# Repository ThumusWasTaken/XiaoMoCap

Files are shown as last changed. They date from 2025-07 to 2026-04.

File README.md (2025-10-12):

Guide to build and code you TOL, tiny open logger IMU sensor:

1- Arduino code folder:
TinyOpenLogger_Code

2- PCB CAD files folder:
KiCad_files

3- 3D print link: 
https://cad.onshape.com/documents/7f3e29c87ee979af035eb522/w/dbec0ba7e6f450b7338eaabc/e/624f816bbdc67f06185ccd3e?renderMode=0&uiState=68eb8f6068579bafa34129be

4- JLC PCB order folder:
JLCorder_withLED

5- Web user interface code folder:
HTMLWebUI

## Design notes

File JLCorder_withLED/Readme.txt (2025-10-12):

These Files are to be used directly on https://jlcpcb.com/

1- Upload the esp_bmi_withLED_GBR.zip in Add gerber file
2- Select wanted PCB options - this is a 2-layer PCB
3- If you wan to add th component assembly, select PCB Assembly and tick Assemble top side
4- Click next twice
5- In section: Bill of Materials, add BOM file: esp_bmi270_mlx90393_withLED and CPL file: esp_bmi270_mlx90393-pos_numbered_withLED.

Note: The Xiao ESP32-C3 is added to the CPL but is not part of the PCB, a window "Project has unselected parts" will show when pressing Next, select "Do not place".
In the window component placement, make sure the purple dots of each component is aligned with the dot/arrow/star on the silkscreen.

Note2: I the case of a component out of stock, look for an alternative on https://jlcpcb.com/parts, make sure the foot print is the same and modify the CPL file with the corresponding JLCPCB Part #.

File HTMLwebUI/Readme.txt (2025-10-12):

WebUI Instructions:

Activate WiFi: Press the Xiao sensor button.
(LED flashes quickly, then turns OFF)
Connect: Join TOL-xxx WiFi network.
Configure:
Use the UI to configure rate and duration and click “Send Config”, or
Long press the sensor button (< 4 sec) to use default config.
(LED ON)
Start Recording: Press the sensor button.
(LED slow flash — WiFi off, data recording)
Stop Recording:
Wait for configured duration, or
Long press (< 4 sec) to stop early.
(LED quick flash — data ready)
Upload Data:
Press button to re-enable WiFi.
Reconnect to TOL-xxx WiFi and click “Connect” on UI.
(LED ON — data is sending)
Download:
Click “Download CSV” to save data early, it will automatically download when complete.
(LED OFF — finished)

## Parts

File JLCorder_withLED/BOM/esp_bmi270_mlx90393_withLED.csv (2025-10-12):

Comment | Designator | Footprint | LCSC Part #
100 nF Unpolarized capacitor | C201,C202,C301,C302,C401 | C_0402_1005Metric | C1525
LED Light emitting diode | D101 | LED_Kingbright_APA1606_1.6x0.6mm_Horizontal | C3034753
220 Resistor | R101 | R_0402_1005Metric | C25091
4.7k Resistor | R201,R202,R203,R401,R402,R403 | R_0402_1005Metric | C25900
XIAO ESP32 C3 | U1 | DIP-14_600_ELL | C19189385
BMI270 | U2 | LGA-14 2.5x3mm | C2836813
MLX90393ELW-ABA-011-RE | U3 | QFN-16-1EP_3x3mm_P0.5mm_EP1.675x1.675mm | C2654971
W25N01GVZEIG | U4 | WSON-8_8X6_WIN | C907680

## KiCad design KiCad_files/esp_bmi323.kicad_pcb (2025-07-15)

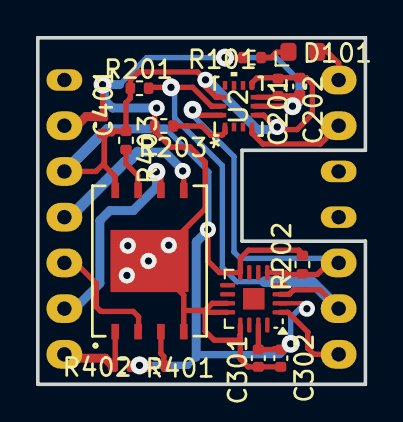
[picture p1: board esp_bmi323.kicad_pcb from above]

Board: 2 copper layers, 18.2 x 19.2 mm, 17 parts (1 on the bottom side), 14 nets.

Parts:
C201, C202, C301, C302, C401: 100 nF; C_0402_1005Metric
D101: LED; LED_Kingbright_APA1606_1.6x0.6mm_Horizontal
R101: 220; R_0402_1005Metric
R201, R202, R203, R401, R402, R403: 4.7k; R_0402_1005Metric
U1: XIAO ESP32 C3; DIP-14_600_ELL
U2: BMI323; BMI323_BOS
U3: MLX90393; QFN-16-1EP_3x3mm_P0.5mm_EP1.675x1.675mm
U4: W25N01GVZEIG; WSON-8_8X6_WIN

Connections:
+3.3V: C201.1, C202.1, C301.2, C302.2, C401.2, R201.1, R202.1, R401.1, R402.1, R403.1, U1.12 (3V3), U2.5 (VDDIO), U2.8 (VDD), U2.12 (CSB), U3.2 (MS/~CS), U3.8 (VDDIO), U3.15 (VDD), U4.8 (VCC)
GND: C201.2, C202.2, C301.1, C302.1, C401.1, R101.2, R203.2, U1.13 (GND), U2.6 (GNDIO), U2.7 (GND), U3.11 (A1), U3.12 (A0), U3.13 (GND), U4.4 (GND), U4.9 (GND)
GPIO7_MLX90393: U1.7 (GPIO7), U3.1 (INT)
GPIO44_W25N: R402.2, U1.8 (RX), U4.1 (/CS)
MISO_W25N: U1.10 (MISO), U4.2 (DO(IO1))
MOSI_W25N: U1.11 (MOSI), U4.5 (DI(IO0))
unnamed: D101.2 (A), U1.1 (GPIO2)
unnamed: D101.1 (K), R101.1
unnamed: R203.1, U2.1 (SDO)
unnamed: R403.2, U4.7 (/HOLD(IO3))
unnamed: R401.2, U4.3 (/WP(IO2))
SCK_W25N: U1.9 (SCK), U4.6 (CLK)
SCL_BMI323: R201.2, U1.6 (SCL), U2.13 (SCX), U3.3 (SCL/SCLK)
SDA_BMI323: R202.2, U1.5 (SDA), U2.14 (SDX), U3.5 (SDA/MOSI)

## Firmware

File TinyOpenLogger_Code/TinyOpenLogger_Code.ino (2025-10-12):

#include <Wire.h>
#include <time.h>
#include "W25N01GV.h"
#include "BadBlockManager.h"
#include "Logger.h"

#include <Arduino_BMI270_BMM150.h>
#include <Adafruit_MLX90393.h>

#include <WiFi.h>
#include <WebServer.h>

// Flash
#define FLASH_CS D7
W25N01GV flash(FLASH_CS);
BadBlockManager bbm(flash);
Logger logger(flash, bbm);

uint32_t data_num = 0;
// Sensors
bool acc_active = true;
bool gyr_active = true;
bool mag_active = true;
uint32_t duration_ms = 60000;       // Default: 60 seconds
uint16_t sample_rate_hz = 10;       // Default: 10 Hz
bool configReceived = false;
Adafruit_MLX90393 mag = Adafruit_MLX90393();

// Switch and LED settings
#define LED_PIN 2        // D0 on XIAO ESP32-C3 (GPIO2)
#define BUTTON_PIN 9     // BOOT button is on GPIO9
volatile bool buttonInterruptTriggered = false;
unsigned long lastInterruptTime = 0;
const unsigned long debounceDelay = 200;  // ms debounce
bool interruptsAllowed = false;
volatile bool longPressDetected = false;
unsigned long buttonPressStart = 0;
bool buttonHeld = false;

// WiFi credentials for Access Point
const char* ssid = "TOL-001";
const char* password = "12345678";

// Configurable IP settings
IPAddress local_IP(192, 168, 1, 100);  // Change this IP as needed
IPAddress gateway(192, 168, 1, 1);
IPAddress subnet(255, 255, 255, 0);

// Create WebServer object on port 80
WebServer server(80);

String dat = "";

void shutdownWiFi() {
  WiFi.disconnect(true);
  WiFi.mode(WIFI_OFF);
  Serial.println("Wi-Fi turned off.");
}

void startWiFi() {
  WiFi.mode(WIFI_AP);                      // Set Wi-Fi mode to AP
  WiFi.softAPConfig(local_IP, gateway, subnet);  // Configure IP
  WiFi.softAP(ssid, password);             // Start AP
  Serial.println("Wi-Fi Access Point restarted");
}


void handleData() {
  server.sendHeader("Access-Control-Allow-Origin", "*");
  server.setContentLength(CONTENT_LENGTH_UNKNOWN);
  server.send(200, "text/csv", "");
  server.sendContent("timestamp,ax,ay,az,gx,gy,gz,mx,my,mz,counter\n");

  uint8_t readBuf[PAGE_SIZE];
  uint32_t lastPage = logger.getCurrentPage();

  for (uint32_t page = 0; page < lastPage; page++) {
    if (!bbm.isBlockGood(page / 64)) continue;
    if (!flash.readPage(page, readBuf, sizeof(readBuf))) continue;

    PageHeader *hdr = (PageHeader*)readBuf;
    if (hdr->magic != PAGE_MAGIC) continue;

    for (uint16_t i = 0; i < RECORDS_PER_PAGE; i++) {
      SensorRecord *rec = (SensorRecord*)(readBuf + HEADER_SIZE + i * RECORD_SIZE);
      if (rec->timestamp == 0xFFFFFFFF) break;

      char line[128];
      int len = snprintf(line, sizeof(line),
        "%lu,%d,%d,%d,%d,%d,%d,%d,%d,%d,%lu\n",
        rec->timestamp,
        rec->ax, rec->ay, rec->az,
        rec->gx, rec->gy, rec->gz,
        rec->mx, rec->my, rec->mz,
        rec->counter);
      server.sendContent_P(line, len);
    }
    delay(1);
  }

  server.sendContent("");
}

void handleLoggingConfig() {
  if (server.hasArg("duration") && server.hasArg("rate")) {
    for (int i = 0; i < server.args(); i++) {
      Serial.printf(" - %s = %s\n", server.argName(i).c_str(), server.arg(i).c_str());
    }

    duration_ms = server.arg("duration").toInt() * 1000UL;
    sample_rate_hz = server.arg("rate").toInt();
    
    acc_active = (server.arg("accelerometer") == "true");
    gyr_active = (server.arg("gyroscope") == "true");
    mag_active = (server.arg("magnetometer") == "true");

    if (duration_ms == 0) duration_ms = 60000;
    if (sample_rate_hz == 0 || sample_rate_hz > 100) sample_rate_hz = 10;

    configReceived = true;

    Serial.printf("✔ Config received: %lu ms, %u Hz\n", duration_ms, sample_rate_hz);
    Serial.printf("✔ Config received: accel: %, gyro: %, magne: %", acc_active, gyr_active, mag_active);
    server.send(200, "text/plain", "✔ Logging config received.");
  } else {
    server.send(400, "text/plain", "❌ Missing 'duration' or 'rate' parameter.");
  }
}

// Function to properly disable SPI to free up GPIO9
void disableSPIForButton() {
  // End SPI communication
  SPI.end();
  // Set CS high to deselect flash
  digitalWrite(FLASH_CS, HIGH);
  // Configure GPIO9 as input with pullup for button
  pinMode(BUTTON_PIN, INPUT_PULLUP);
  // Small delay to let pin settle
  delay(10);
  
  Serial.println("SPI disabled, GPIO9 configured for button");
}

// Function to re-enable SPI for flash access
void enableSPIForFlash() {
  // Reconfigure SPI
  SPI.begin();
  // Reinitialize flash
  flash.setSPIFrequency(1000000);
  // Set CS as output and select flash
  pinMode(FLASH_CS, OUTPUT);
  digitalWrite(FLASH_CS, LOW);
  // Small delay to let SPI settle
  delay(10);
  
  Serial.println("SPI re-enabled for flash access");
}

void IRAM_ATTR handleButtonPress() {
  if (!interruptsAllowed) return;  // Ignore until setup is done

  unsigned long currentTime = millis();
  if ((currentTime - lastInterruptTime) > debounceDelay) {
    buttonInterruptTriggered = true;
    lastInterruptTime = currentTime;
  }
}

void setup() {
  //Serial.begin(115200);
  Serial.begin(921600);
  delay(1000);
  Serial.println("Starting multi-sensor NAND logger...");

  // I2C setup (Xiao ESP32-C3: SDA = 8, SCL = 9)
  Wire.begin();
  Wire.setClock(400000);
  delay(100);

  // --- Flash setup ---
  flash.setSPIFrequency(1000000);
  if (!flash.begin()) {
    Serial.println("Flash init failed!"); while (1);
  }
  flash.clearBlockProtection();
  flash.setECCEnabled(true);
  bbm.scan();
  if (!logger.begin()) {
    Serial.println("Logger init failed!"); while (1);
  }

  Serial.println("Erasing flash... this may take a few seconds.");
  logger.eraseAll();
  Serial.println("Flash erase complete.");

  // Set initial time
  struct tm timeinfo;
  timeinfo.tm_year = 2025 - 1900;
  timeinfo.tm_mon = 5;
  timeinfo.tm_mday = 30;
  timeinfo.tm_hour = 14;
  timeinfo.tm_min = 0;
  timeinfo.tm_sec = 0;
  time_t t_of_day = mktime(&timeinfo);
  struct timeval now = { .tv_sec = t_of_day };
  settimeofday(&now, NULL);

  // --- BMI270 init ---
  if (!IMU.begin()) {
    Serial.println("BMI270 not detected!");
    while (1);
  }
  Serial.println("BMI270 connected!");
  Serial.print("Accelerometer rate = ");
  Serial.println(IMU.accelerationSampleRate());
  Serial.print("Gyroscope rate = ");
  Serial.println(IMU.gyroscopeSampleRate());

  // --- MLX90393 init ---
  if (!mag.begin_I2C()) {
    Serial.println("MLX90393 not detected!");
    while (1);
  }
  Serial.println("MLX90393 connected.");
  mag.setGain(MLX90393_GAIN_1X);
  mag.setResolution(MLX90393_X, MLX90393_RES_16);
  mag.setResolution(MLX90393_Y, MLX90393_RES_16);
  mag.setResolution(MLX90393_Z, MLX90393_RES_16);
  mag.setOversampling(MLX90393_OSR_0);
  mag.setFilter(MLX90393_FILTER_2);

  delay(10);

  // Configure Access Point with custom IP
  WiFi.softAPConfig(local_IP, gateway, subnet);
  WiFi.softAP(ssid, password);
  
  IPAddress IP = WiFi.softAPIP();
  
  Serial.println("=== ESP32 Data Server Started ===");
  Serial.println("WiFi SSID: " + String(ssid));
  Serial.println("WiFi Password: " + String(password));
  Serial.println("Server IP: " + IP.toString());
  Serial.println("Endpoints:");
  Serial.println("  http://" + IP.toString() + "/data (CSV)");
  Serial.println("  http://" + IP.toString() + "/json (JSON)");
  Serial.println("===================================");

  // Set up web server routes
  //server.on("/", handleRoot);
  server.on("/data", handleData);
  server.on("/send", handleLoggingConfig);

  // Start server
  server.begin();
  Serial.println("HTTP server started");

  
  //Internal LED setup
  pinMode(LED_PIN, OUTPUT);
  digitalWrite(LED_PIN, LOW);  // Ensure it's off initially
  //Boot button setup
  pinMode(BUTTON_PIN, INPUT_PULLUP);
  // Wait for button to be released and settle
  while (digitalRead(BUTTON_PIN) == LOW) {
    Serial.println("Waiting for button release...");
    delay(50);
  }
  // Small delay to ensure pin settles
  delay(100);
  // Attach interrupt but don't allow it to trigger yet
  attachInterrupt(digitalPinToInterrupt(BUTTON_PIN), handleButtonPress, FALLING);
  // Set debounce timer
  lastInterruptTime = millis();
}
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

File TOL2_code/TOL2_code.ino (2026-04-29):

/**
 * BMI270 IMU Logger with SdFat  |  XIAO ESP32S3
 * ─────────────────────────────────────────────
 * Uses SdFat instead of the built-in SD library.
 * SdFat writes in 512-byte aligned blocks which avoids
 * the partial-write corruption seen with the SD library
 * on long recordings.
 *
 * Libraries (Arduino Library Manager):
 *   - Arduino_BMI270_BMM150
 *   - SdFat  by Bill Greiman
 *
 * Wiring:
 *   BMI270  SDA → D4,  SCL → D5  (I2C)
 *   SD      CS  → D2,  SCK → D7, MOSI → D9, MISO → D8
 *
 * Serial Monitor: 921600 baud
 */

#include <Wire.h>
#include <SPI.h>
#include <Arduino_BMI270_BMM150.h>
#include "Adafruit_MLX90395.h"
#include "SdFat.h"
#include "esp_timer.h"   // int64_t µs — no rollover


// ── SD pins ───────────────────────────────────────────────────────────────────
#define SD_CS_PIN SS
#define SPI_CLOCK   SD_SCK_MHZ(16)   // 16 MHz — safe for most SD cards

// ── Log file ──────────────────────────────────────────────────────────────────
#define LOG_FILE   "data.csv"

// ── Flush every N samples ─────────────────────────────────────────────────────
#define FLUSH_EVERY   100

SdFat  sd;
SdFile logFile;

Adafruit_MLX90395 mag = Adafruit_MLX90395();

// ── Adjust BMI/BMM ranges ─────────────────────────────────────────────────────

#define BMI270_ADDR  0x68   // SDO → GND = 0x68,  SDO → VCC = 0x69

void setAccelRange(uint8_t range) {
  // range: 0=±2g  1=±4g  2=±8g  3=±16g
  Wire.beginTransmission(BMI270_ADDR);
  Wire.write(0x41);    // ACC_RANGE register
  Wire.write(range & 0x03);
  Wire.endTransmission();
  float ranges[] = {2, 4, 8, 16};
  Serial.printf("Accel range set to ±%.0fg\n", ranges[range & 0x03]);
}

void setGyroRange(uint8_t range) {
  // range: 0=±2000  1=±1000  2=±500  3=±250  4=±125  dps
  Wire.beginTransmission(BMI270_ADDR);
  Wire.write(0x43);    // GYR_RANGE register
  Wire.write(range & 0x07);
  Wire.endTransmission();
  float ranges[] = {2000, 1000, 500, 250, 125};
  Serial.printf("Gyro range set to ±%.0f dps\n", ranges[range & 0x07]);
}


// ─────────────────────────────────────────────────────────────────────────────
void setup() {
  Serial.begin(921600);
  while (!Serial) delay(10);
  Serial.println("\n=== BMI270 SdFat Logger ===");

  // I2C for BMI270
  Wire.begin();
  Wire.setClock(400000);

  if (!IMU.begin()) {
    Serial.println("BMI270 not found! Halt.");
    while (1);
  }
  Serial.println("BMI270 OK");
  Serial.print("Accelerometer rate = ");
  Serial.println(IMU.accelerationSampleRate());
  Serial.print("Gyroscope rate = ");
  Serial.println(IMU.gyroscopeSampleRate());
  //setAccelRange(1);   // ±4g
  //setGyroRange(0);    // ±2000 dps

  // --- MLX90393 init ---
  if (!mag.begin_I2C()) {
    Serial.println("MLX90395 not detected!");
    while (1);
  }
  Serial.println("MLX90395 connected.");
  //uint8_t gain_val 7;
  
  Serial.print("Gain: "); Serial.println(mag.getGain());
  Serial.print("Resolution: "); Serial.println(mag.getResolution());
  Serial.print("OSR: "); Serial.println(mag.getOSR());
    // mag.setResolution(MLX90395_RES_16);
    // mag.setOSR(MLX90395_OSR_1);
    //mag.setFilter(MLX90395_FILTER_2); //?
  //mag.setResolution(MLX90395_RES_16);   // finest LSB — already set
    //mag.setOSR(MLX90395_OSR_2);           // can work for freq up to 100Hz
    //mag.setOSR(MLX90395_OSR_0);            // default value
  //mag.setGain(5);                        // safe for Earth-field sensing

  // SdFat init
  Serial.print("Initializing SD card...");

  if (!sd.begin(SD_CS_PIN)) {
    Serial.println("initialization failed!");
    return;
  }
  Serial.println("initialization done.");
}

// ─────────────────────────────────────────────────────────────────────────────
void loop() {

  // ── Ask for duration ─────────────────────────────────────────────────────────
  Serial.println("\nDuration in seconds:");
  uint32_t duration_ms = readInt() * 1000UL;
  if (duration_ms == 0) duration_ms = 60000UL;

  // ── Ask for sample rate ───────────────────────────────────────────────────────
  Serial.println("Sample rate in Hz (1-100):");
  uint16_t hz = (uint16_t)readInt();
  if (hz == 0 || hz > 100) hz = 10;

  int64_t interval_us = 1000000LL / hz;
  Serial.printf("Logging %lu s @ %u Hz\n", duration_ms / 1000UL, hz);

  // ── Open file ─────────────────────────────────────────────────────────────────
  sd.remove(LOG_FILE);
  if (!logFile.open(LOG_FILE, O_WRONLY | O_CREAT | O_TRUNC)) {
    Serial.println("Cannot open file!");
    return;
  }

  // Write CSV header
  // logFile.println("timestamp_ms,ax_mg,ay_mg,az_mg,gx_ddps,gy_ddps,gz_ddps,n");
  logFile.println("timestamp_ms,ax_mg,ay_mg,az_mg,gx_ddps,gy_ddps,gz_ddps,mx,my,mz,n");

  // ── Timing ───────────────────────────────────────────────────────────────────
  int64_t nextTick_us = esp_timer_get_time();
  int64_t end_us      = nextTick_us + (int64_t)duration_ms * 1000LL;

  float    ax, ay, az, gx, gy, gz, mx, my, mz;
  mx=0, my=0, mz=0;
  uint32_t n = 0;
  char     buf[128];

  Serial.println("Recording...");

  // ── Hot loop ──────────────────────────────────────────────────────────────────
  while (esp_timer_get_time() < end_us) {

    // Wait for next sample slot
    while (esp_timer_get_time() < nextTick_us) {}
    int64_t ts_us = nextTick_us;   // capture before advancing
    nextTick_us  += interval_us;

    // Read sensors
    IMU.readAcceleration(ax, ay, az);
    IMU.readGyroscope(gx, gy, gz);
    mag.readData(&mx, &my, &mz);

    // Serial.print("X: "); Serial.print(mag.magnetic.x);
    // Serial.print(" \tY: "); Serial.print(mag.magnetic.y); 
    // Serial.print(" \tZ: "); Serial.println(mag.magnetic.z); 


    // Format line — snprintf, no String, no heap allocation
    int len = snprintf(buf, sizeof(buf),
      "%lu,%d,%d,%d,%d,%d,%d,%d,%d,%d,%lu",
      // "%lu,%d,%d,%d,%d,%d,%d,%lu",
      // (unsigned long)(ts_us / 1000LL),
      // (int16_t)(ax * 1000), (int16_t)(ay * 1000), (int16_t)(az * 1000),
      // (int16_t)(gx * 100),  (int16_t)(gy * 100),  (int16_t)(gz * 100),
      // (int16_t)(mx * 10),   (int16_t)(my * 10),   (int16_t)(mz * 10),
      // (unsigned long)n);
     (unsigned long)(ts_us / 1000LL),
      (int16_t)(ax), (int16_t)(ay), (int16_t)(az),
      (int16_t)(gx),  (int16_t)(gy),  (int16_t)(gz),
      (int16_t)(mx),   (int16_t)(my),   (int16_t)(mz),
      (unsigned long)n);

    logFile.write(buf, len);
    logFile.write('\n');

    Serial.println(buf);

    n++;
    if (n % FLUSH_EVERY == 0) logFile.sync();   // SdFat uses sync() not flush()
  }

  // ── Close ─────────────────────────────────────────────────────────────────────
  logFile.sync();
  logFile.close();
  Serial.printf("Done — %lu samples written.\n\n", (unsigned long)n);
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

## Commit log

2025-07-06 Rename esp_bmi323-JLCPCB Assembly Order.xls to JLCorder/esp_bmi323-JLCPCB Assembly Order.xls
    [esp_bmi323-JLCPCB Assembly Order.xls]
2025-07-06 Update and rename esp_bmi323.csv to JLCorder/BOM/esp_bmi323.csv
    [esp_bmi323.csv]
2025-07-15 Add files via upload
    improved UI with CSV auto-save
    future version append the current csv file
2025-09-30 Create esp32_csv_GUI_NEW.html
    new GUI format, only captures the data, is compatible with the next release of W25N01GV_test_readwrite.ino
2025-09-30 Update W25N01GV_test_readwrite.ino
    included bmi and mlx data capture codes.
    included wifi and server creation to transfer the data.
    the function handleData is a new version and is compatible with the html GUI: esp32_csv_GUI_NEW or cmd line: curl http://192.168.1.100/data > dump.csv
    reduced interval base value to reach higher data rates (but still far from expected one)
    Added an option to input yes or no to pull the data several times.
2025-10-03 new working file with all sensors on, data rate above 100Hz acheivable and interval timing working
2025-10-06 Update esp32_csv_GUI_NEW.html
    added section to input duration and rate and select which sensors to use in the GUI
2025-10-09 added all LED and switch settings, corrected the ti,ing interval within the loop, tried to correct some int definitions
2025-10-11 jlc order new files
    [esp_bmi323-B_Cu.gbr, esp_bmi323-Edge_Cuts.gbr, esp_bmi323-F_Cu.gbr, esp_bmi323-F_Silkscreen.gbr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]
2025-10-11 reorganising the git
    [esp_bmi323-JLCPCB Assembly Order.xls, esp_bmi323-pos_numbered.xlsx, esp_bmi323.csv]
2025-10-12 updated to available sensor on jlc
    [esp_bmi323_withLED.csv]
2025-10-12 modified for bmi270, and added instructions in read me
    [esp_bmi270_mlx90393-pos_numbered_withLED.xlsx, esp_bmi270_mlx90393_withLED.csv, esp_bmi323_withLED.csv]
2025-10-12 Delete JLCorder_withLED/BOM/esp_bmi323_withLED.csv
    bmi323 version
    [esp_bmi323_withLED.csv]
2025-10-12 Delete JLCorder_withLED/CPL/esp_bmi323-pos_numbered_withLED.xlsx
    wrong file with 323
    [esp_bmi323-pos_numbered_withLED.xlsx]
2025-10-12 Update and rename esp32_csv_GUI_NEW.html to TOL_wifi_to_csv_GUI.html
2025-10-12 TinyOpenLogger_Code add
    Adding code with rest of ESP at end of each loop and LED/switch setting fitting the paper's finite state machine
2025-10-12 Update TinyOpenLogger_Code.ino
    stop wifi at start of script to save battery
